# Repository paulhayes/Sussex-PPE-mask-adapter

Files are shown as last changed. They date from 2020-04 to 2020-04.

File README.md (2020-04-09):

# PPE Mask 
An adaptor that enables the addition of an HME filter to a widely available snorkelling full face mask. 

Creators of adaptor:
https://customsurgical.de/en/free-3d-model-for-customizing-a-virus-protection-mask/

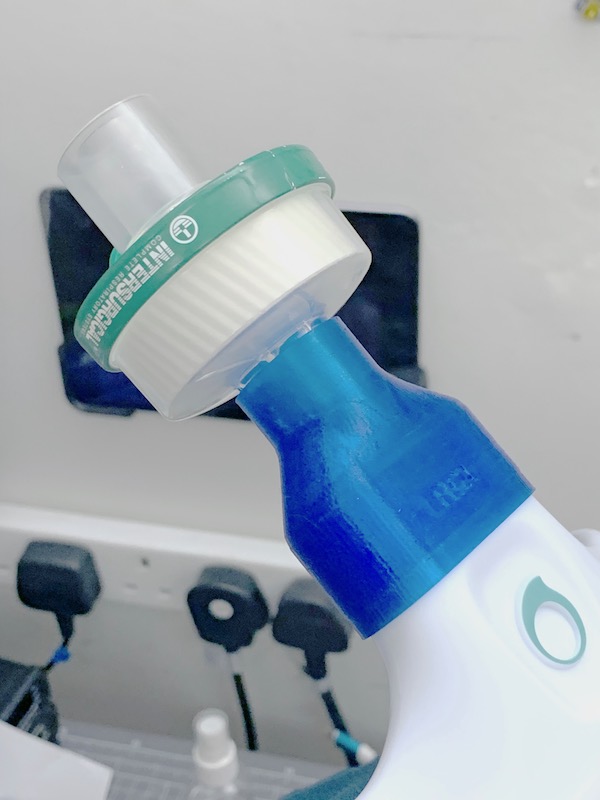
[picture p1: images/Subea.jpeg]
Subea adaptor


We have completely redesigned this adaptor from the original above. 

* Compact and faster to print
* No hard corners, very smooth and therefore easier to clean
* Remove the embossed logo (props to the original team but this isn't needed and makes it more difficult to sterilise)
* Redesign filter connector to make a tighter seal

Subea Easy Breathe version : 
* Lip at the snorkel connector that wraps around the O ring

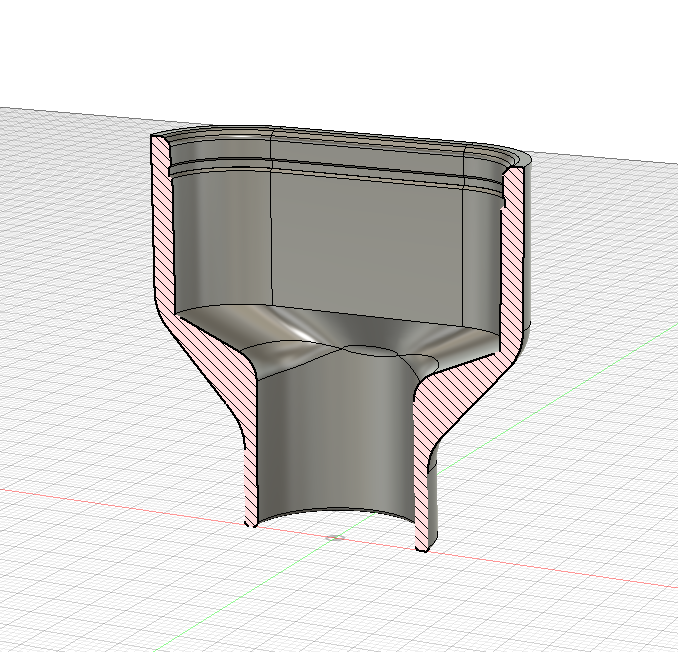
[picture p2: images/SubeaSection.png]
Subea cross section


Leucothea version (chinese snorkel):
* Slight raised lips on the inside that surround the rubber gasket

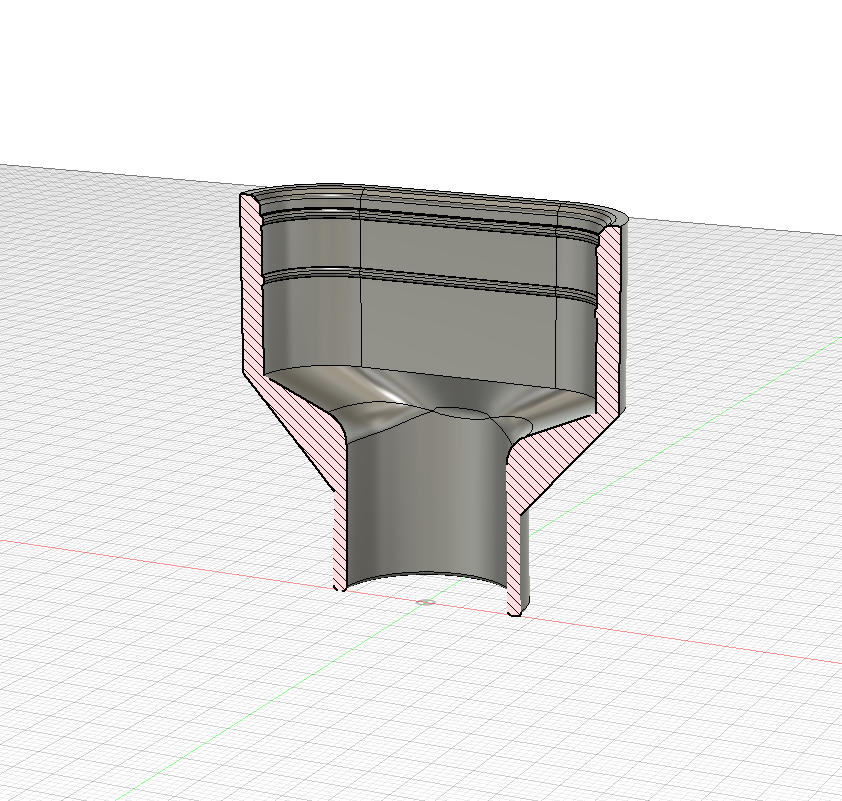
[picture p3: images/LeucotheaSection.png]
title


# Printer Settings

* PETG or PET filament

* 0.2 layer height, 20% infill (we used gyroid but any infill pattern will likely be acceptable)
* 4 perimeters - this is important as the clip section needs to be solid
* 0.45 extrusion width
* 5 solid layers bottom
* Orientation - print so the circular narrow section is on the bottom, clip at the top

Use vaseline to make the seals airtight. Note that the version information is etched onto the model to be an aid when slicing; it is not deep enough to be visible when printed (unless your 3D Printer is high resolution). 

# TOLERANCES

Please ensure that your 3D printer is dimensionally accurate and use callipers to measure your adaptor. 

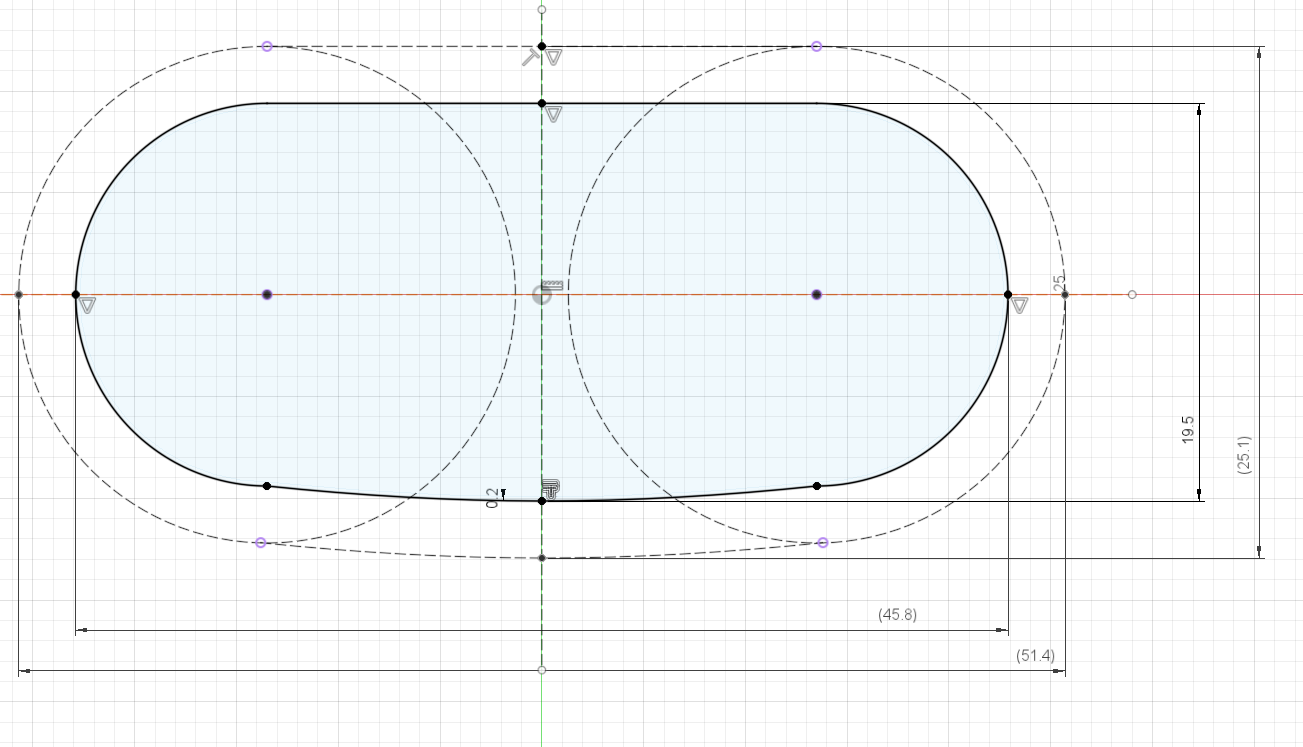
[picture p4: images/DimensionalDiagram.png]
Dimensional Diagram


# SAFETY NOTES

In our testing, we found there to be some inconsistency as to whether the front valve lets in air. You need to do your own testing on your masks. More information here : https://docs.google.com/document/d/1C-w77MgJVmBnwxqWTOj560orCjCVPEXkqCZU_f2qz8c/edit

### Sterile Handling notes

* Use Nitrile gloves.
* Clean with 70% isopropyl alcohol, or soap and water. Put in sealed bag.

### FRONT FACE FILTER ADAPTOR

We have also designed an experimental adaptor for attching to the front of the mask. See the sub-folder *SnorkelFrontAdaptor* for more information. 

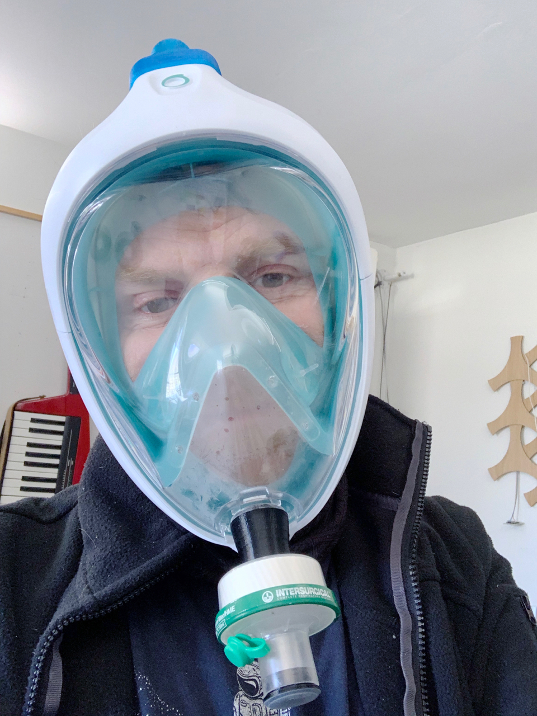
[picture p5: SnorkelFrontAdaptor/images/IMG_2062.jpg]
Front face filter worn


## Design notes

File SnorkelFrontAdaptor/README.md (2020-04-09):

# Subea snorkel front face medical filter adaptor 

An experimental design that enables the addition of an HME filter to the front valve of a Subea EasyBreathe snorkel, to be used in addition to the filter adaptors fitted to the top of the mask.  

NB This is very much a proof-of-concept design that requires further development.

Front face filter worn

The adaptor comprises three parts, the inner back plate on the inside of the mask, the adaptor between the mask and the filter, and the valve adaptor on the other side of the filter. 

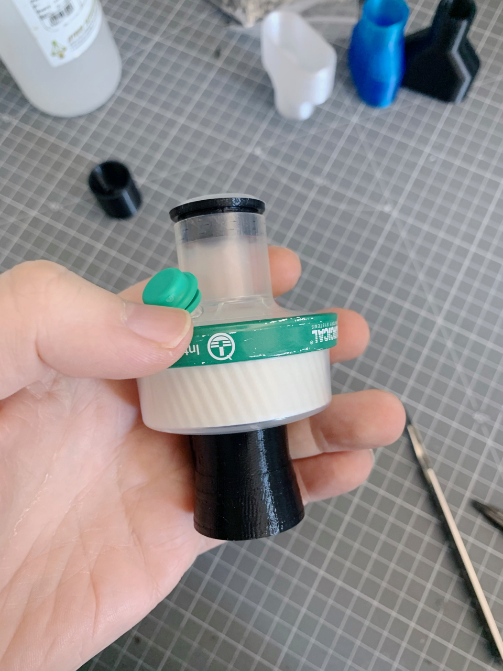
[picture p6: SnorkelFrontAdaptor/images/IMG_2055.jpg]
Front face filter adaptor


It requires a standard 25mm x 2.5mm o-ring, an M3 threaded insert and a M3 x 10mm screw. 

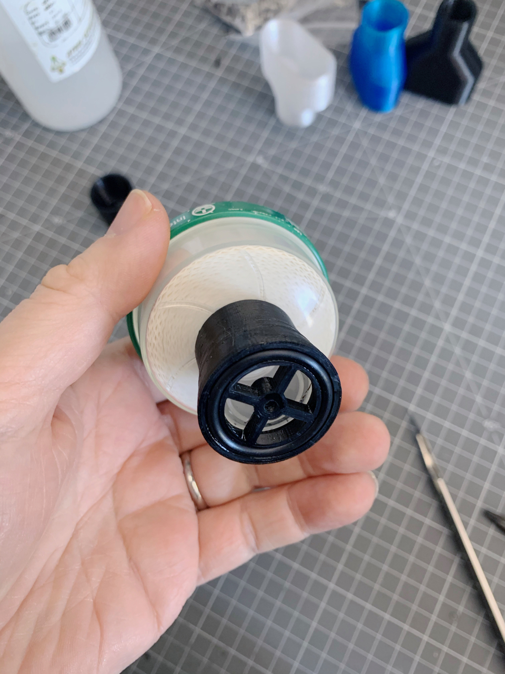
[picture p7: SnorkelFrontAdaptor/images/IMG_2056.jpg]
O ring end of the adaptor


The insert is placed inside the adaptor, and the screw comes through the back plate on the inside and out of the front of the snorkel. 
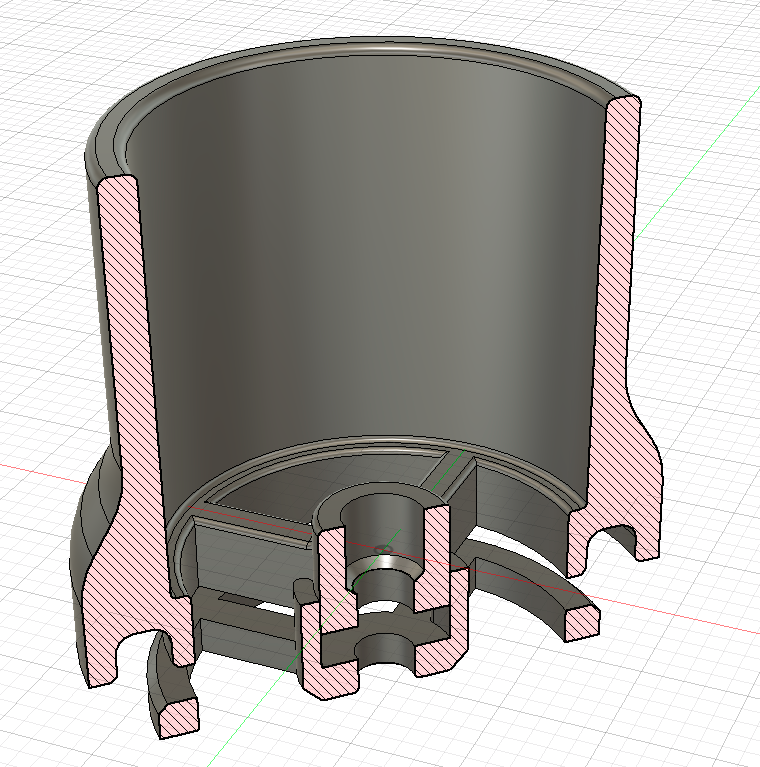
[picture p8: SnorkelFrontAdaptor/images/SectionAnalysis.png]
Section analysis

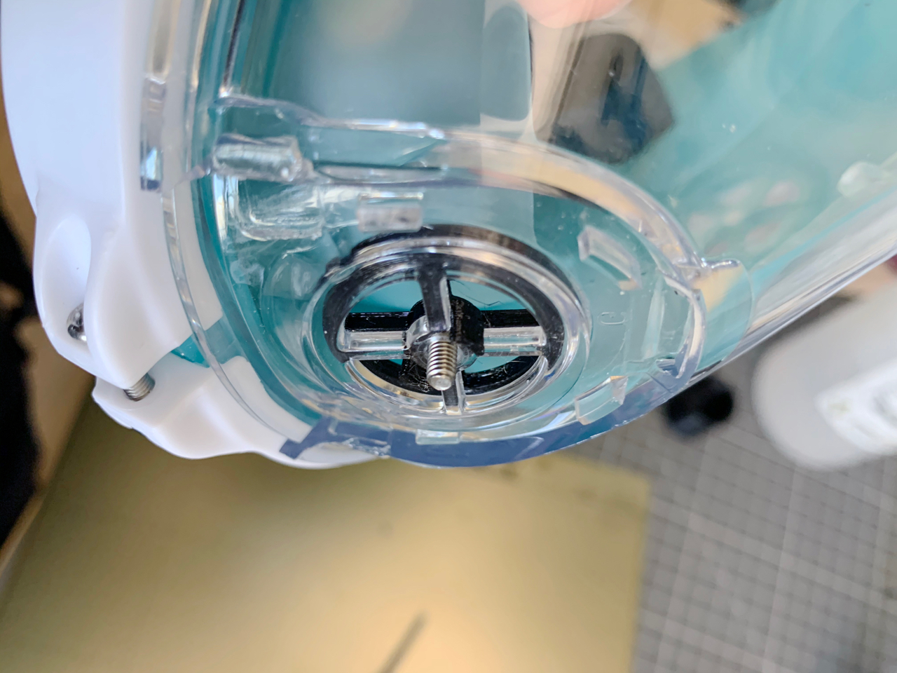
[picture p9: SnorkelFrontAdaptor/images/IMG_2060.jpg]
M3 screw protruding from inside


The valve adaptor goes on the other side of the filter. 

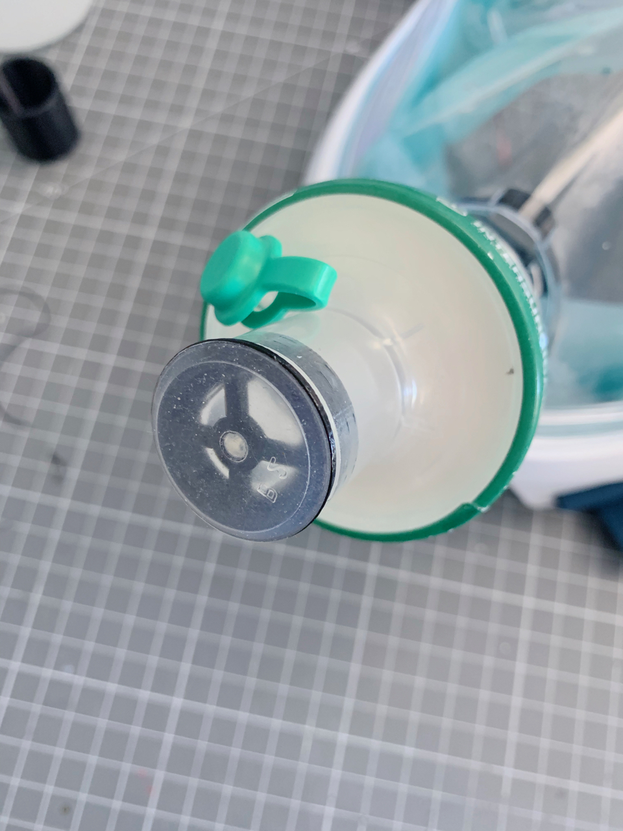
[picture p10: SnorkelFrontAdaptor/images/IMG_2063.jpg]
Valve connection


# Design notes

The inner back plate has struts that are easily broken, until we can develop the design further, we urge that you treat these gently, or else print the back plate with an SLA resin printer. 

# Printer Settings

* PETG filament recommended. 

Use vaseline to make the seals airtight. 

### Steril Handling notes

* Use Nitrile gloves.
* Clean with 70% isopropyl alcohol, or soap and water. Put in sealed bag.

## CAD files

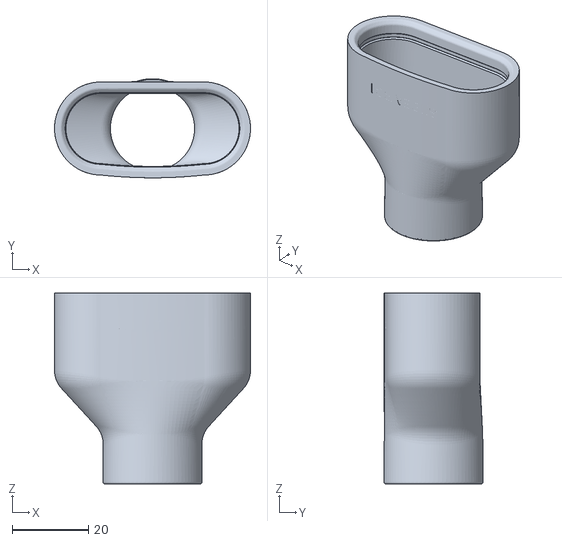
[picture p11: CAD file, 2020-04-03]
SnorkelAdaptorSubeaRC1.stl
51.4 x 26.1 x 50.0

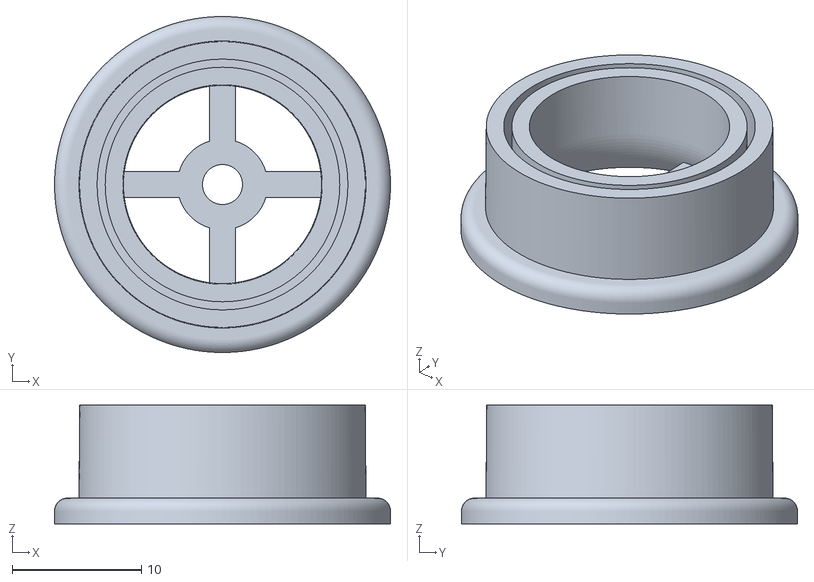
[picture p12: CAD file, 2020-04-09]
SnorkelFrontAdaptor/SnorkelAdaptorFront_v11_FilterValveAdaptor_.stl
26.0 x 26.0 x 9.20

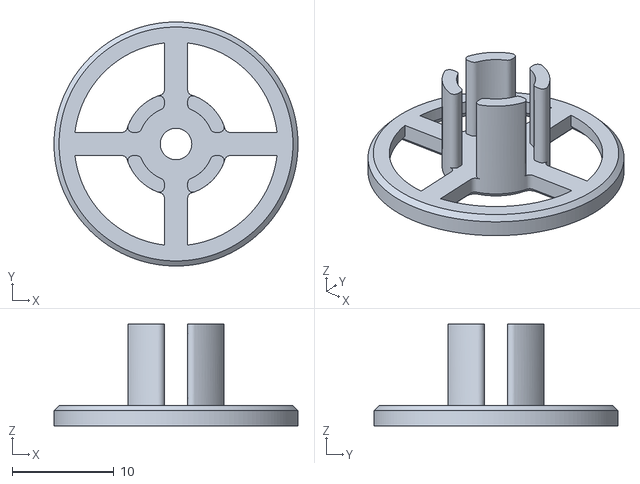
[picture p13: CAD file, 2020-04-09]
SnorkelFrontAdaptor/SnorkelAdaptorFront_v11_InsidePlate_.stl
24.0 x 24.0 x 10.0

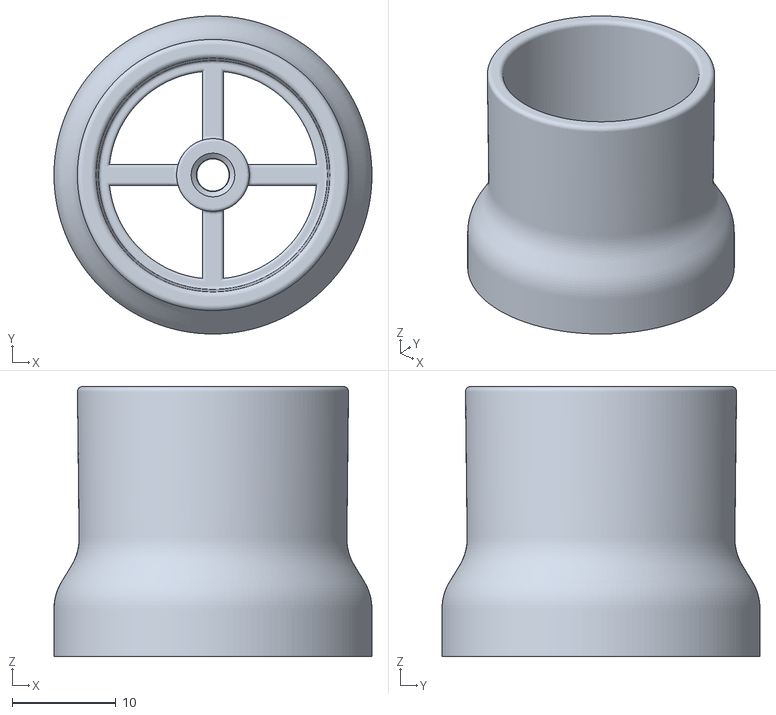
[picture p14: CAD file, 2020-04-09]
SnorkelFrontAdaptor/SnorkelAdaptorFront_v11_SnorkelAttachment_.stl
30.6 x 30.6 x 26.0

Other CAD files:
SnorkelAdaptorLeuc02.stl

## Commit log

2020-03-24 Delete adaptador_mascara.stl
    Deleting original file so people don't accidentally use this one instead of the new one
    [adaptador_mascara.stl]
2020-03-25 Add STL version 0.12
    [SnorkelAdaptor.stl]
2020-03-25 Upload correctly named STL file
    [Sussex-PPE-Mask-Adaptor-v012.stl]
2020-03-29 Uploaded v013 - has a thinner bendier clip
    [Sussex-PPE-Mask-Adaptor-v013.stl]
2020-03-29 Adding 3mf file for v013
    [Sussex-PPE-Mask-Adaptor-v013.3mf]
2020-03-31 Seb's latest model
    [SnorkelAdaptorv18.stl]
2020-04-03 RC1 of the Subea adaptor
    V0.02 of the Leuk adaptor
    [SnorkelAdaptorLeuk02.stl, SnorkelAdaptorSubeaRC1.stl]
2020-04-09 Front filter adaptor images, rename STL
    [SnorkelAdaptorLeuc02.stl]
2020-04-09 Update front adaptor readme, and upload STLs
    [SnorkelAdaptorFront_v11_FilterValveAdaptor_.stl, SnorkelAdaptorFront_v11_InsidePlate_.stl, SnorkelAdaptorFront_v11_SnorkelAttachment_.stl]
